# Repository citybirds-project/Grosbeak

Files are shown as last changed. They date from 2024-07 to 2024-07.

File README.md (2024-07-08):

# Grosbeak Bioacoustics Microphone
An open-source horn microphone for bioacoustics specializing in capturing nocturnal flight calls of migratory birds.

The Grosbeak Bioacoustics Microphone was created by J'orge Garcia in collaboration with Benjamin M. Van Doren, Madison Chudzik, and Sara Lipshutz, and Jocelyn Brito for nocturnal flight call monitoring from rooftops in Chicago, IL.

## Build Materials
- 3D-printed Horn, Seal, and Grill using ASA Filament
- 12" x 12" sound-dampening foam, cut in half
- Polypropylene or polyethylene tape
- 80-gauge cling wrap
- 4" zip ties or 6" zip ties (UV-resistant)
- 14" zip ties or 24" zip ties (UV-resistant)
- Heavy-duty UV-resistant rubber band
- Acoustically transparent mesh 
- 2" x 0.04" felt strip

## Build Instructions
1. Turn the Horn so it's facing upward.
2. Line the inside with 2, 12x6in pieces of sound-dampening foam and fold any excess inward
3. Use small zip ties to secure the horn to the seal.
4. Trim the zip ties.
5. Flip the horn over and cut a swatch of 8 gauge wrap large enough to hang halfway down the sides
6. With two people, have one person hold the wrap taught while the other tapes down each wall with four pieces of poly tape.
7. Use additional tape as necessary, and finish with a final warp around all four walls.
8. Grab the 3D-printed grill and stick felt pieces on each corner base.
9. Carefully sit the grill on top of the horn.
10. From the bottom, loop the long zip tie through the vertically aligned holes, connecting the seal to the horn to the grill. DO NOT TIGHTEN
11. Once all four zip ties are installed, give all four equal tension, making slow adjustments to each side until the unit is completely secured.
12. Trim the zip ties
13. Cut a piece of 20x20 mesh.
14. Lay mesh over the grill as evenly as possible and secure it with a UV-resistant rubber band over the top.
15. Install your microphone element.
16. Use the mounting features with appropriate zip ties to secure the microphone to your recording device and environment.

## 3D Print Settings  
**Recommended printer:**  
Bambu Lab Carbon X1  

**Filament type:**  
ASA

**Orientation:**  
Horn down

**Walls:**  
4
 
**Infill:**  
25%, Triangles  

**Support:**  
Tree(auto)

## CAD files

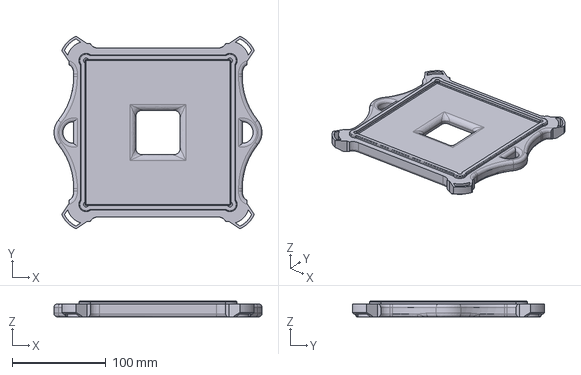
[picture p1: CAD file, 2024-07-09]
Grosbeak - seal.v1.21.step
222.0 x 205.3 x 17.0 mm

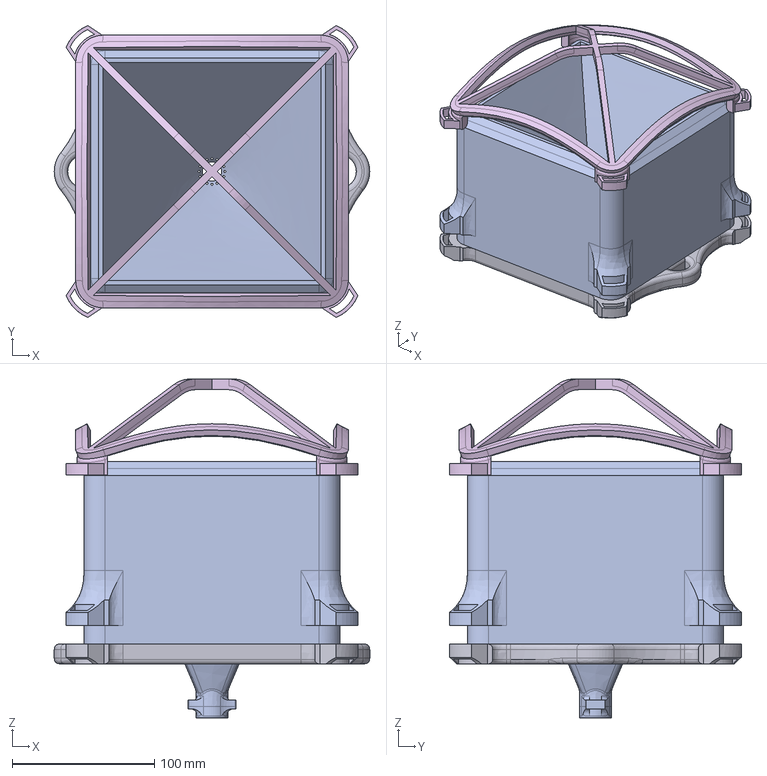
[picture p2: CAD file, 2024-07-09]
Grosbeak_Microphone_All_Parts_0.93.step
222.0 x 205.3 x 238.5 mm

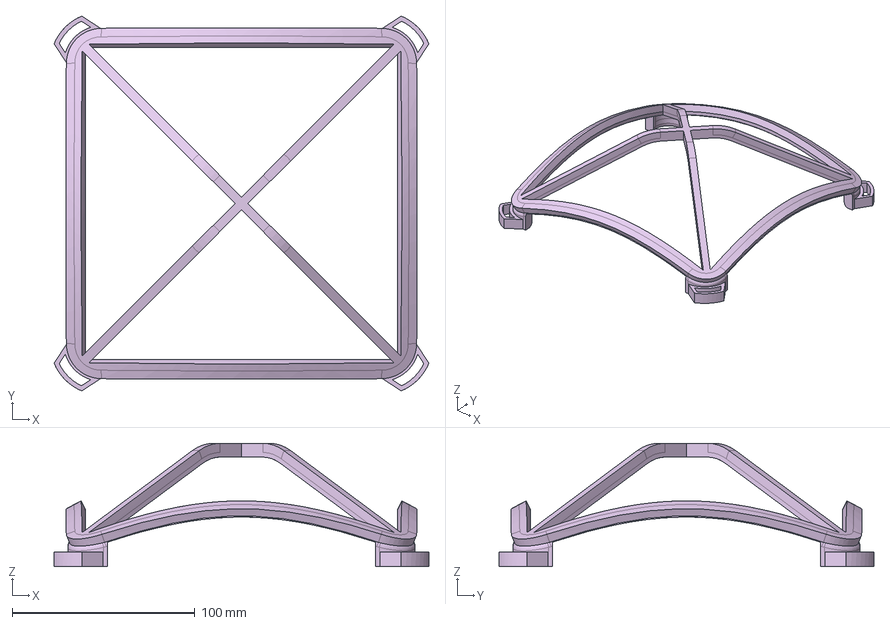
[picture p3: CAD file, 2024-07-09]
Grosbeak - grill.v1.step
205.3 x 205.3 x 67.5 mm

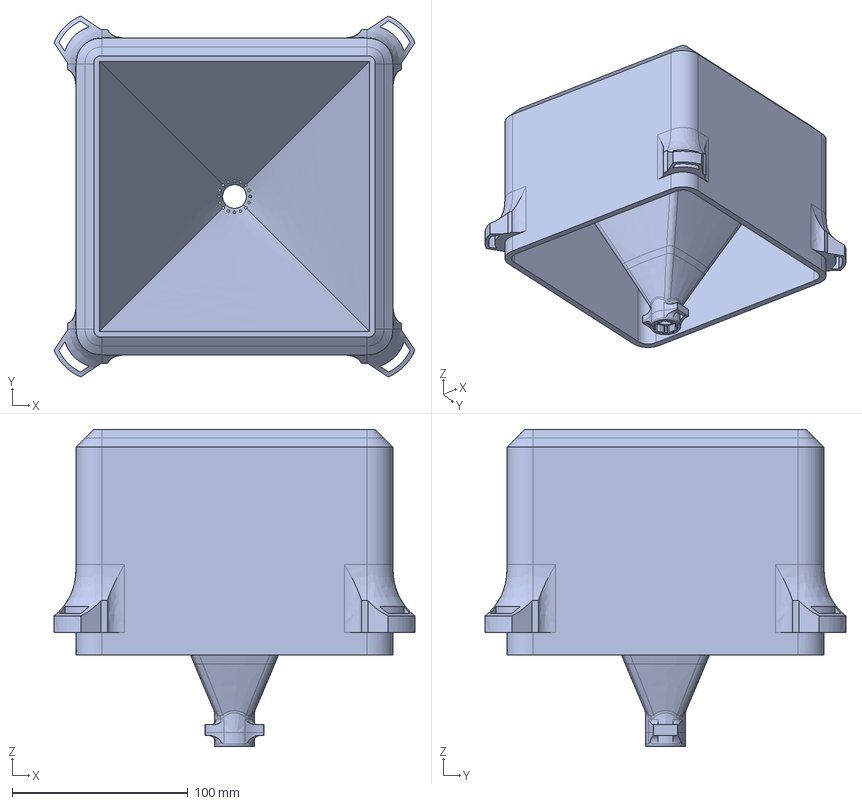
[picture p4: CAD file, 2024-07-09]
Grosbeak - horn.v0.93.step
205.3 x 205.3 x 180.5 mm

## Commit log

2024-07-08 Materials, print, and build notes
    Added acknowledgement, materials, build instructions, and print settings.
2024-07-09 Initial upload of STEP files
    Uploading the STEP files for the horn, seal, and grill parts of the Grosbeak Microphone.
    [Grosbeak - grill.v1.step, Grosbeak - horn.v0.93.step, Grosbeak - seal.v1.21.step, Grosbeak_Microphone_All_Parts_0.93.step]
